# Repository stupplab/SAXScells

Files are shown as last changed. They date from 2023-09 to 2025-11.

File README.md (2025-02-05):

# SAXScells

This is a repository hosting the CAD files for the liquid sandwich cells used by Stupp lab at NSLS-II 16-ID LIX, APS 5-ID-D DND-CAT and other beamlines. These are mostly meant for aqueous solutions.

## List of Materials

- 3M 9474LE 300LSE double-adhesive sheet (available at Amazon)
- CLAREX PMMA sheet (Precision cast acrylics, available from Astra Products)
- Alkaline-free ultrathin glass, 10mm x 100mm for strips and 100mm x 100mm for plates
  - 30um for minimum background (only available in 100mm x 100mm): we have tested Schott AF32eco for this.
  - 50 or 100um for typical samples: we have tested Schott AF32eco, but others have used Corning Willow glass. We will be testing Nippon Electric Glass G-leaf soon.
    - Update 2024/1: Nippon Electric Glass G-leaf shows similar positional reproducibility for both thickness (WAXS intensity) and roughness (SAXS parasitic scattering) as Schott AF32eco.
    - Acidic or basic solutions can etch glass and produce near-beamstop artifacts. Consider using the fillable cells for those.
- Marble stone for pressing: we used the cheese slicer board from Amazon without handle/wire.
https://www.amazon.com/Fox-Run-Marble-Cheese-Replacement/dp/B0000VZA2W
- Texwipe TX3211
- Scotch tape
- Pipettes (30-40uL), air-displacement or positive displacement
- Wide-bore pipette tips or positive displacement pistons

The patterns are laser cut on:
- tape: 3M 9474LE 300LSE
- spacer: 1 mm CLAREX PMMA sheet
- strip / plate: 1.5-2 mm CLAREX PMMA sheet (this depends on path length requirements)

SOP.txt shows the procedure for filling 2mm "strip" cells.

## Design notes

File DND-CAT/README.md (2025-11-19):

**DND-CAT now has a 4 x flat15 cell adapter! Please use flat15 under LIX folder instead. The info below is obsolete.**

This plate / strip setup is compatible with the sample environment at APS 5-ID-D DND-CAT beamline. The sample plate / 9-strip holder is secured on the beamline using the 96x2 well plate holder. Use `w150_stage` to initialize the plate setup, and `w135_stage` to initialize the 9-strip holder.

```
\\plate1.do
\\row is from A to J for 150 cell, A to I for 135 cell (9 strips)
\\column is 1 to 15, notch is drawn on the plate

area_detectors_set_param("SampleThickness",0.234)
snapshoton
for (mycellrow=asc("A");mycellrow<=asc("I");mycellrow++) {
 area_detectors_take_background
 for (mycellcol=1;mycellcol<=15;mycellcol++) {
  printf("%c %d\n",mycellrow,mycellcol)
  eval(sprintf("w135_samp %d %d",mycellrow,mycellcol))
  swcollectexpert
  mvr samp_v 0.75;waitmove
  swcollectexpert
  mvr samp_v 0.75;waitmove
  swcollectexpert
 }
}
```

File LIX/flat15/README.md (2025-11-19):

# flat15 cells
*NSLS-II LIX and DND-CAT compatible glass window cells for solution scattering*

This design is compatible with the automatic sample exchanger robot at NSLS-II LIX beamline. Place the frame-like "spacer" piece on top of the aluminum base plate, then place the sample strip on top. The notch should be placed toward the door when mounted on the beamline (notch is close to the handle).
```
mc_measure_holder('samples-proc.xlsx','<strip name>',exp=<exposure time>, scan=True,check_sname=True,cell_format='flat15')
```
2023/12: For 2023-3 cycle, we tested the mesh scan with robotic arm sample exchange:
```
mc_auto_measure_samples('samples-proc.xlsx',configName='a1',cell_form='flat15',scan='mesh',xrange=1,offset_y=0.5) #configName is defined as a set of strips with their holder positions in the auto-exchanger
```
throughput ~ 11.5 min / 15 samples at LIX with 1s exposure time, 24 frames in flyscan mode. 9 min / 15 samples with 0.5 s/frame, 24 frames.

At DND-CAT, 
```
hidebeam;stage_out
w15x4_stage
show_beam
qdo plate1.do
```
where plate1.do looks like:
```
area_detectors_set_param("SampleThickness",0.234)
snapshoton
for (mycellrow=asc("A");mycellrow<=asc("D");mycellrow++) {
 area_detectors_take_background
 for (mycellcol=1;mycellcol<=15;mycellcol++) {
  printf("%c %d\n",mycellrow,mycellcol)
  eval(sprintf("w15x4_samp %d %d",mycellrow,mycellcol))
  mvr samp_v 0.5;waitmove
  swcollectexpert
  mvr samp_v 0.75;waitmove
  swcollectexpert
  mvr samp_v 0.75;waitmove
  swcollectexpert
 }
}
```

**File description:**

- slot_guide.stl: 3D model of a guide to place the double adhesive tape to the strip. We find it not very necessary (alignment by eye is usually sufficient), but if you are having difficulty applying the tape straight, this may help.
- spacer_brookhaven.svg: 2D vector file for spacing between the aluminum arm and the sample strips to prevent the glass from contacting the aluminum. This should be laser-cut out of 1mm thick cast acrylic plate (or anything thicker than tape + glass, and is uniform in thickness).

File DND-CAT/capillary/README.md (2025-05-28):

# Capillary sorting tip
To fit Charles Supper 1.5 mm capillaries into the DND-CAT multicapillary heater holders, do the following:
## Things to prepare
- Fisherbrand SureOne micropipette tips, 200uL universal fit, 02-707-422
- Ruler
- Fresh razor blade
- Silicone rubber mat
- Marker
## Making the capillary sorter
Using the fresh razor blade, cut the pipette tip at the following length:
- short: 40.5 mm
- long: 41 mm
You can make a series of capillary sorters by cutting them 0.5 mm apart, from 39 mm down to 44 mm.
## Sorting capillaries
Using the capillary sorter you made, you are now passing each capillary through. Look for straight capillaries (no bulging, fluting) that passes the short sorter, but stops with the long sorter. You can group capillaries in numbers.

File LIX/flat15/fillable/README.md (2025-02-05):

Fillable cells: users bring solutions in microcentrifuge tubes, along with assembled cell strips. 

tape_brookhaven_fillable.svg: the red lines need to be cut at lower power to cut only two layers out of 3 (smooth protective layer + adhesive layer). Cut the red lines first with ~1mm lead-in / lead-out, then cut the black lines.

Assembly: remove the smooth protective layer and attach the tape to the acrylic strip on both sides. Removal of the other protective layer should remove the tab-like adhesives above the u-shaped wells.

At the beamline, the following workflow is executed:
- Mount the empty strips on aluminum brackets, with 1mm spacer bracket in-between.
- Place the empty strips on the robot parking area, ~8 at a time.
- Measure empty cells.
- Fill the strips with samples, then place back on the robot parking area
- Measure filled cells, and perform empty subtraction.
- Subtract corresponding buffer.
A typical strip measurement with 24 frames, 1s / frame exposure takes about 11-12 minutes. This means the sample throughput is ~1 min / cell. The downside is the halved throughput and possible contamination if cells are not kept clean. Sample evaporation can be a concern if you are running samples with robots.

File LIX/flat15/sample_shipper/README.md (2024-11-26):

3D printed sample shipper, meant for non-hazardous samples.

**File description**

- centrifuge_rack_v1.stl, racklid_2mm_v1.1.stl: 3D model of a storage rack / centrifugation adaptor to remove bubbles from the samples. Use a 96-well plate swinging bucket holder (deep form factor). We print ours with PLA with support at the bottom, infill of 15% with gyroids, 0.3mm draft resolution in a Prusa MK3S+ FDM printer.

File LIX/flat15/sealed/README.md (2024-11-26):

**File description**

- strip_brookhaven.svg: 2D vector file for the main compartment for flat15 cells. This should be laser-cut out of cast acrylic plates with known thickness. Area per cell = 17.034 mm^2.
- tape_brookhaven.svg: 2D vector file for the double adhesive tape for flat15 cells. This should be laser-cut applied to both sides of the main compartment strip.

*Experimental*
- stripT_brookhaven.svg and tapeT_brookhaven.svg: T-shaped cell to reduce volume and focus on sedimented materials. May not work on 2mm thick spacers due to the beam hitting the PMMA walls. The bottom of the cell is at the same height, the top is 1mm higher. Tape is centered against the T. Area per cell = 14.009 mm^2.

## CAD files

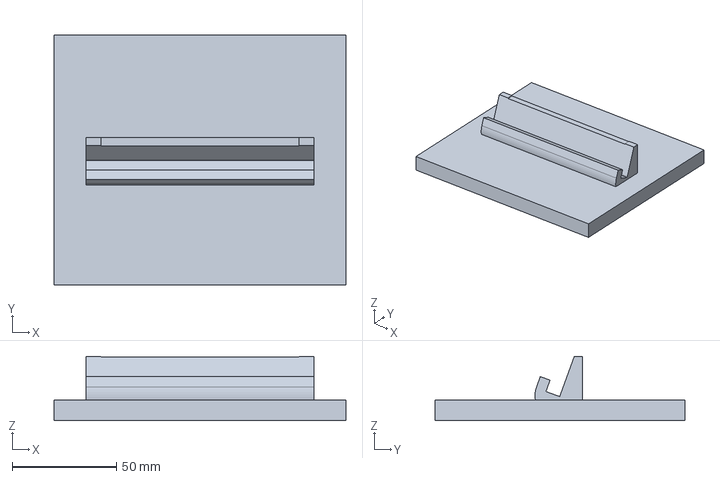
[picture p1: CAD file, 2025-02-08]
LIX/flat15/fillable/cradle_v2.FCStd
140.0 x 120.0 x 30.8 mm

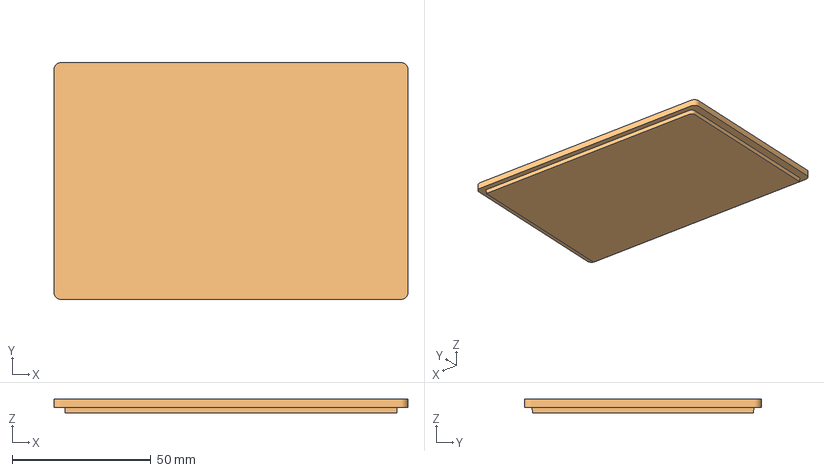
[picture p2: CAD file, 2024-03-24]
LIX/flat15/sample_shipper/racklid.FCStd
127.8 x 85.5 x 5.00 mm
Body (Meshed)

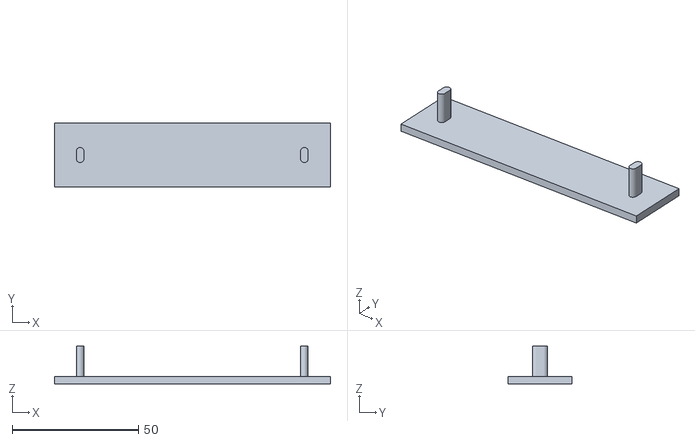
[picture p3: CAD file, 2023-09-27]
LIX/flat15/slot_guide.stl
109.4 x 25.4 x 15.0

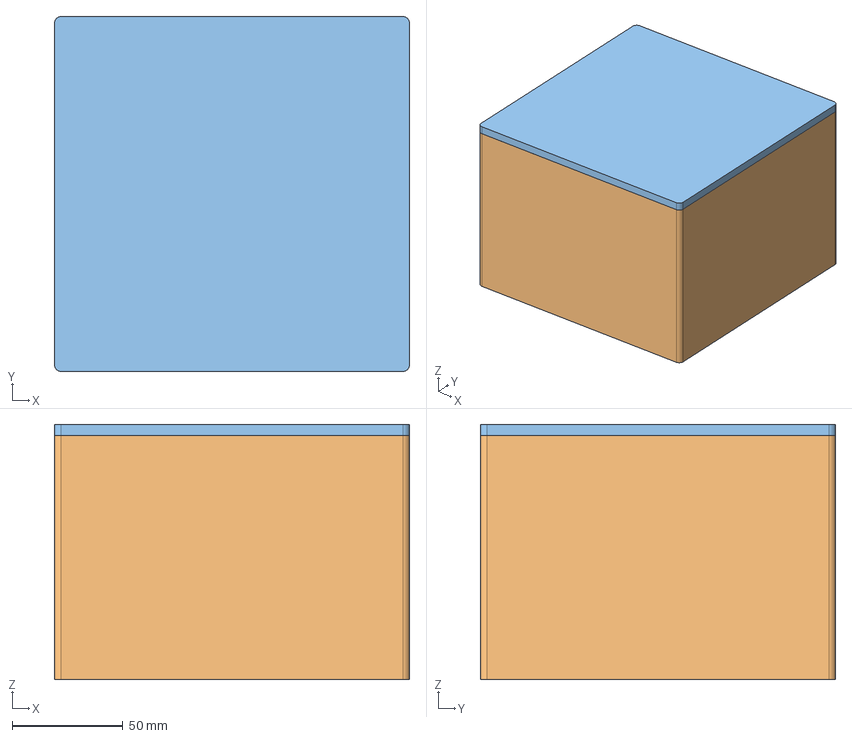
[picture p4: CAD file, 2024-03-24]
misc/NEG_glassbox/glass_box.FCStd
160.0 x 160.0 x 115.0 mm
Inner_sleeve
Lid

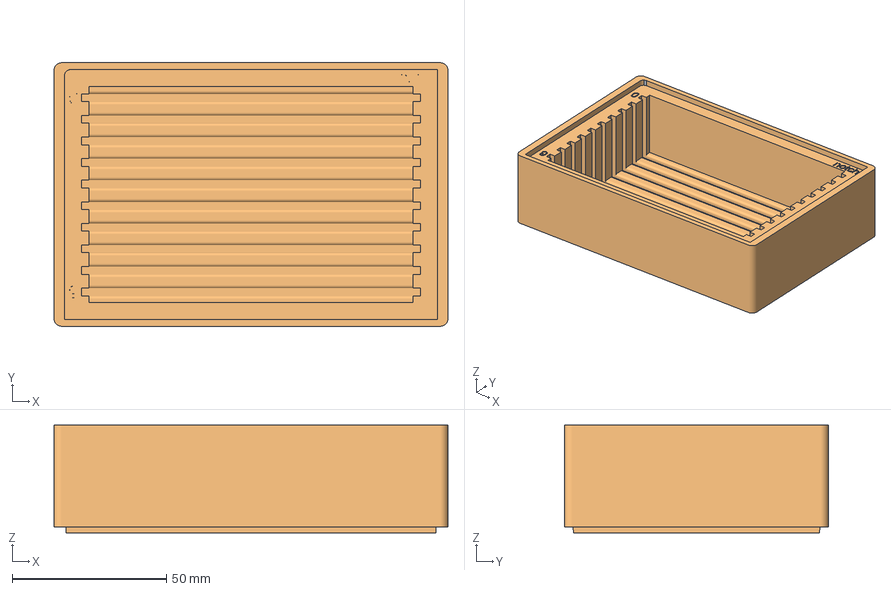
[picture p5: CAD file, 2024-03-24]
LIX/flat15/sample_shipper/centrifuge_rack_2mm.FCStd
127.8 x 85.5 x 35.0 mm
Pocket005 (Meshed)

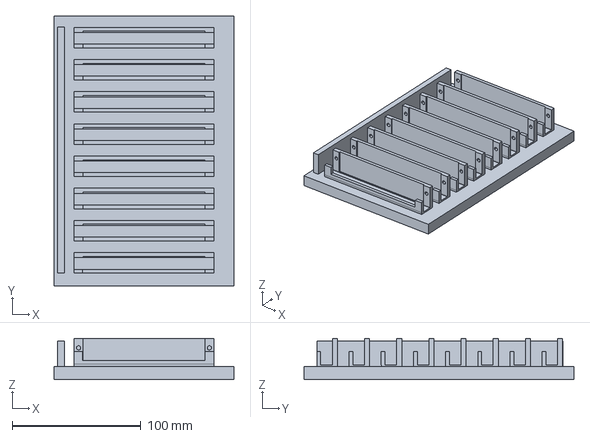
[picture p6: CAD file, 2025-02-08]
LIX/flat15/fillable/parking.FCStd
140.0 x 210.0 x 32.0 mm

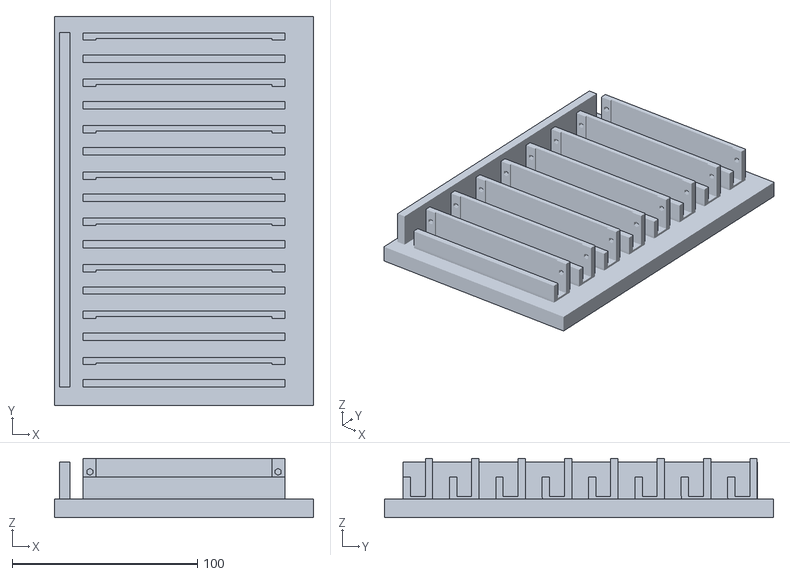
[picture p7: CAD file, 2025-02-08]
LIX/flat15/fillable/parking_v2.stl
140.0 x 210.0 x 32.0

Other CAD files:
LIX/flat15/fillable/20 degrees_v2.stl
LIX/flat15/sample_shipper/centrifuge_rack_2mm.stl
LIX/flat15/sample_shipper/racklid.stl

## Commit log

2023-09-26 Rename strip_brookhaven_v2.svg to LIX/strip_brookhaven.svg
    LIX holder - sample cell
2023-09-27 Add files via upload
    Guide for adhering tape to strip, 3D printing model
    [slot_guide.stl]
2023-10-16 restructured folders in LIX to create folder corresponding to the geometry name
    [slot_guide.stl]
2024-03-24 updated rack slot size for increased tolerance
    [centrifuge_rack.FCStd, centrifuge_rack.stl, centrifuge_rack_v1.stl, glass_box.FCStd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]
2024-03-24 updated filenames
    [centrifuge_rack_2mm.FCStd, centrifuge_rack_2mm.stl, racklid.FCStd]
2024-11-25 Rename LIX/flat15/racklid.FCStd to LIX/flat15/sample_shipper/racklid.FCStd
    moved the file
    [racklid.FCStd]
2024-11-25 file moved
    organized files
    [centrifuge_rack_2mm.FCStd, centrifuge_rack_2mm.stl, racklid.stl]
2025-02-04 Update strip_brookhaven.svg
    Added legible dimensions, adjusted screw hole dimensions. You may need to adjust kerf offsets to adjust the hole size.
2025-02-04 Geometry modification + specify dimension
    Corrected for hole position errors, modified XML code to specify dimensions
2025-02-04 Update stripT_brookhaven.svg
    Shifted T cell up 0.5mm to match with aluminum frame bottom
2025-02-08 Add files via upload
    Added 3D models for sample holder "parking" fixture and cradle for loading samples
    [20 degrees_v2.stl, cradle_v2.FCStd, parking.FCStd, parking_v2.stl]
